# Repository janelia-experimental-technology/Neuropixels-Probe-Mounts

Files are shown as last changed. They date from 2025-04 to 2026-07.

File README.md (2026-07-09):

# Neuropixels-Probe-Mounts

Neuropixels probes are next-generation electrodes that record the activity of hundreds of neurons in the brain. They were developed through a collaboration funded by Howard Hughes Medical Institute, Wellcome Trust, Gatsby Charitable Foundation, and Allen Institute for Brain Science. The head of the collaboration is Tim Harris at HHMI Janelia Research Campus, and the electrodes are designed and fabricated by IMEC, the nanoelectronics research center. Further details may be found in the Harris lab, the University College London, and the Neuropixels home. 

Among the most annoying, time-consuming, and risky tasks when using these and similar Si probes is mounting the probe to a stereotaxic rod or a head post attached to a stereotaxic rod.  The dimensional accuracy of Neuropixels offers the opportunity to use the base as a mounting reference. To facilitate this, the latest versions of Neuropixels now ship with integrated dovetail mounting fixtures.  The fixture orients to the “metal cap,” actually a dovetail mounting adapter.

The technologies offered here are the accessories for mounting these probes and the mounting rod to dovetail adapter for several versions of these probes. These accessories were designed at HHMI's Janelia Research Campus by the Janelia Experimental Technologies group in collaboration with IMEC and end users. The first generation of Neuropixels, 1.0, had a prototype (3A) and production (3B) version. Designs for these versions include the probe holder or mounting rod, the dovetail mount, and the dovetail extension.  We also make available the accessories and assembly for Neuropixels 2.0, including the probe holder/mounting rod, dovetail mount, rod adapter, and assembly instructions. PDF and CAD files are included for convenience.

Opportunity: Free to make for Non-Profit Research by downloading the design here. See included hardware license.
Rights and designs available for Commercial License. Janelia makes no endorsements or guarantees of licensee products.

Neuropixel probes are available from IMEC: Neuropixels.org

Advantages: These accessories allow use of probes that did not originally ship with integrated dovetail mounting features. 

Construction: See the individual part drawings for more detail on fabricating each part. See the attached assembly models for the purchased commercial items needed to complete each probe assembly.

For inquiries, please contact innovation@janelia.hhmi.org and reference this repository.

To cite the designs, please use DOI: https://doi.org/10.25378/janelia.28810037

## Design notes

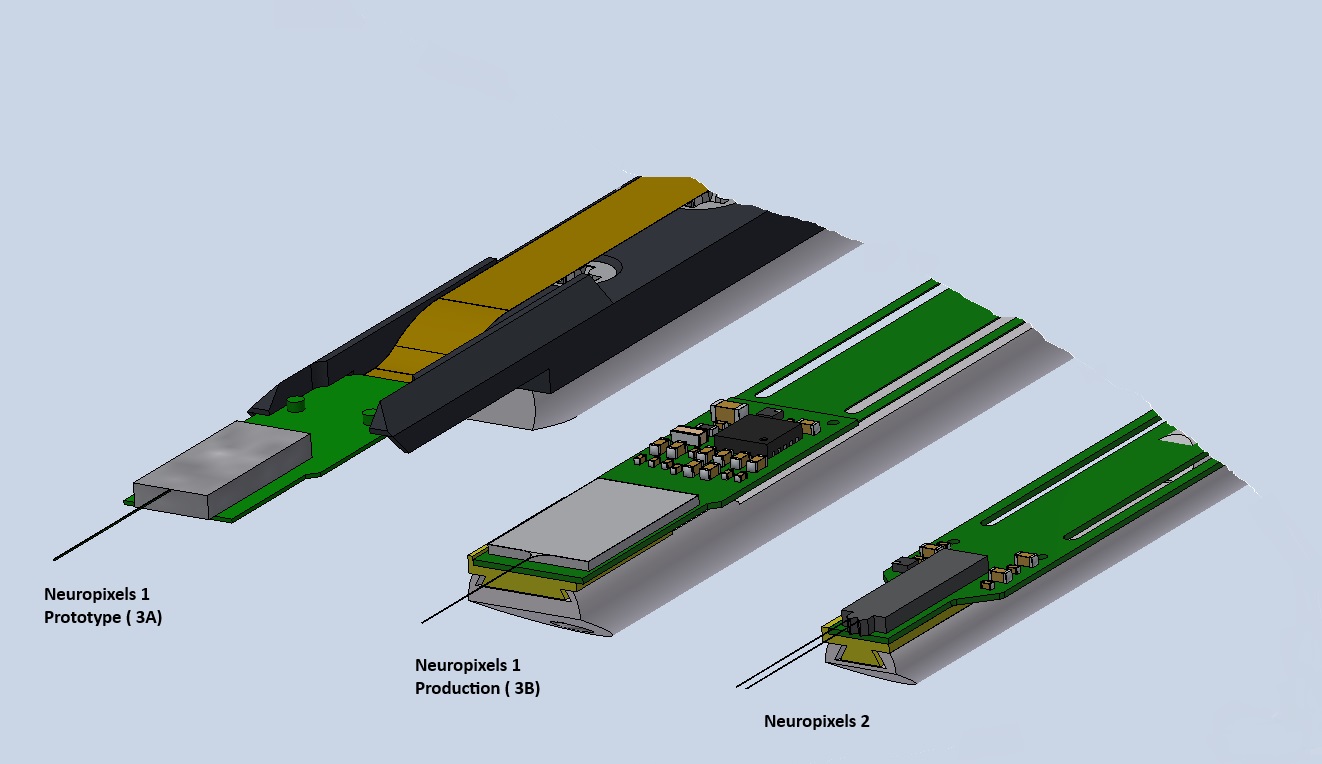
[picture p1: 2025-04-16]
Neuropixels Probe Comparison.jpg

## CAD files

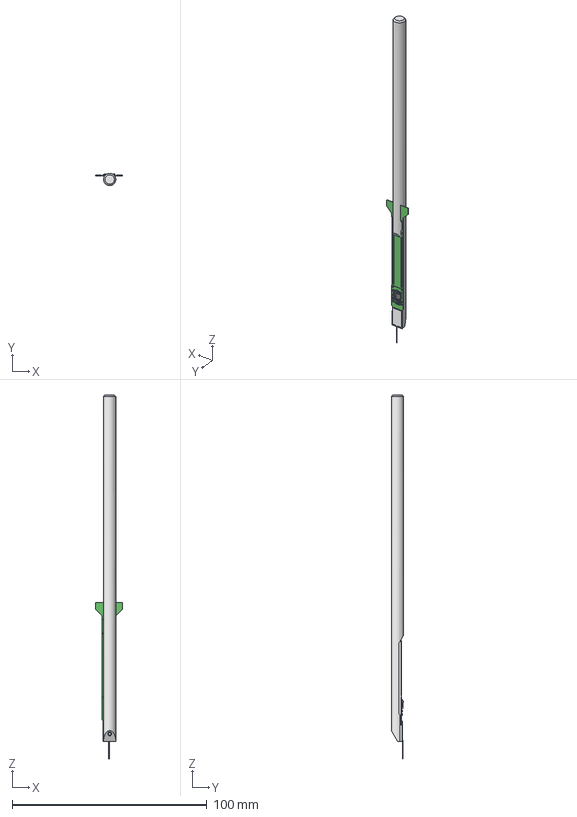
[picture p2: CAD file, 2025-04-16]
Neuropixels-1-Production-Mounts-3B/ASSEMBLY DRAWING AND MODEL/NEUROPIXELS GEN 1 PROBE ASSY 3B.stp
13.8 x 6.35 x 186.9 mm
J007778
J007869
NP2_FLEX_00-01
MISUMI SSHHI-SUS-M2.5-2.5

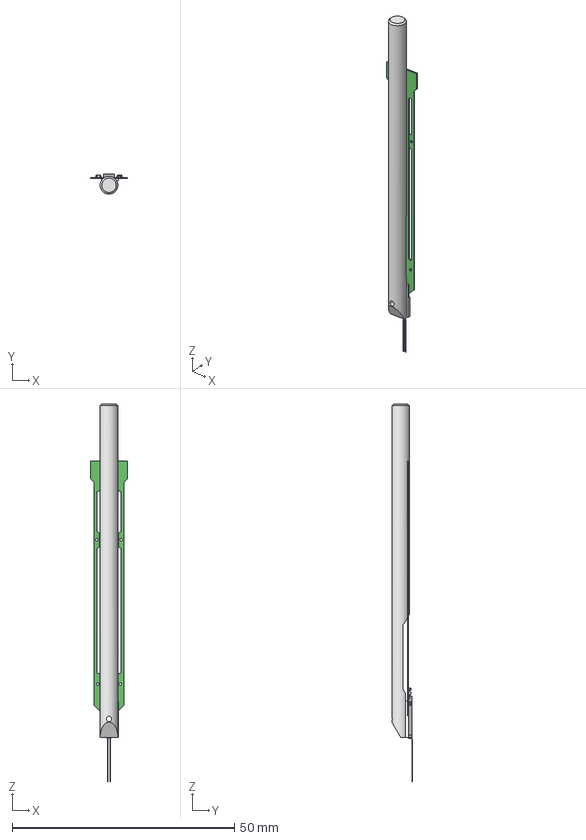
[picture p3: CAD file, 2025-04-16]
Neuropixels-2-Production-Mounts/ASSEMBLY DRAWING AND MODEL/NEUROPIXELS GEN 2 PROBE ASSY.stp
8.40 x 4.57 x 85.0 mm
J008040
J008039
NPM_FLEX_00-00

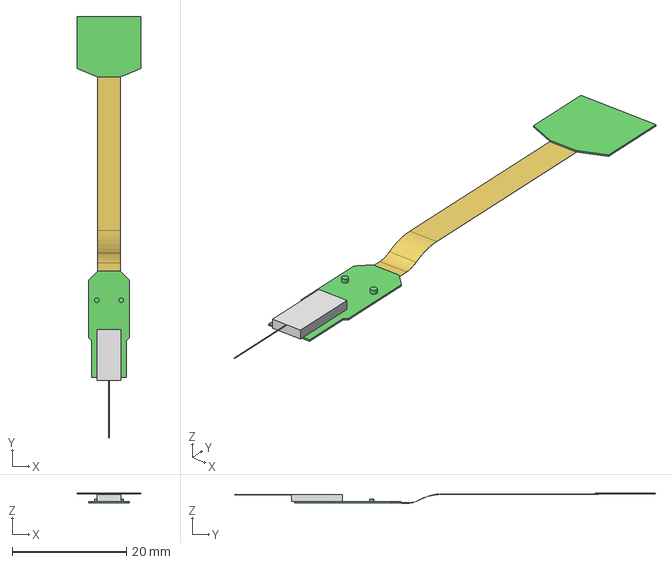
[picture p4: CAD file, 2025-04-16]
Neuropixels-1-Prototype-Mounts-3A/PART DRAWINGS AND MODELS/Neuropixels 1-3A Probe.stp
11.2 x 73.6 x 1.75 mm

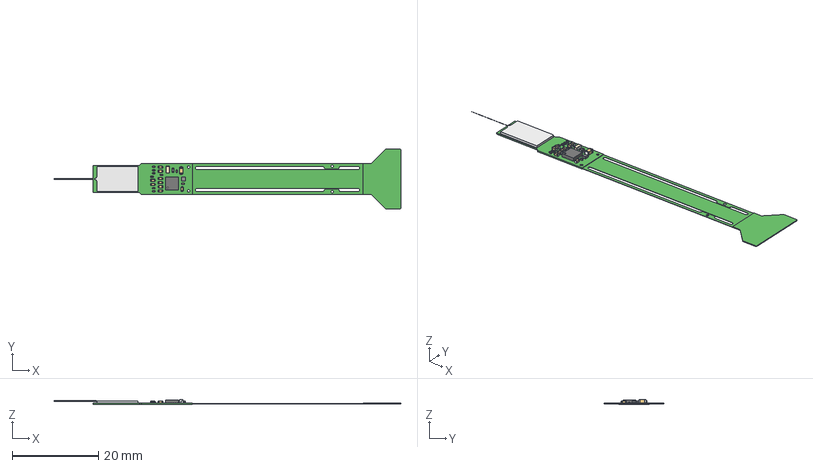
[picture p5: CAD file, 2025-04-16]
Neuropixels-1-Production-Mounts-3B/PART DRAWINGS AND MODELS/Neuropixels 1-3B Probe NP2_FLEX_00-01.stp
80.4 x 13.8 x 1.10 mm

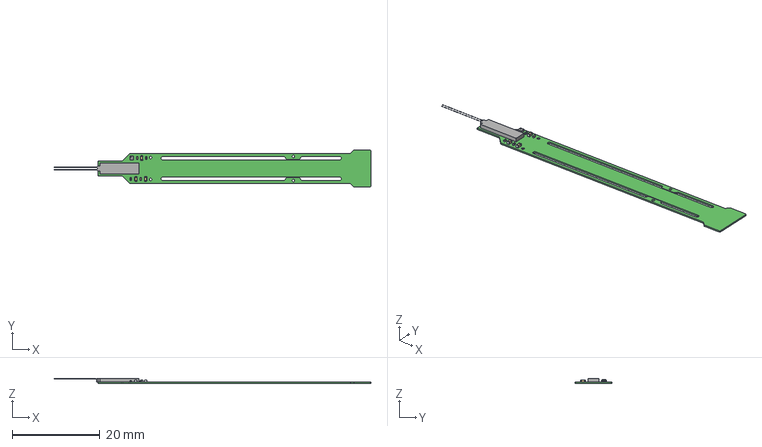
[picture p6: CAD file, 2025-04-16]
Neuropixels-2-Production-Mounts/PART DRAWINGS AND MODELS/Neuropixels 2-Probe NPM_FLEX_00-00.stp
72.2 x 8.40 x 1.10 mm

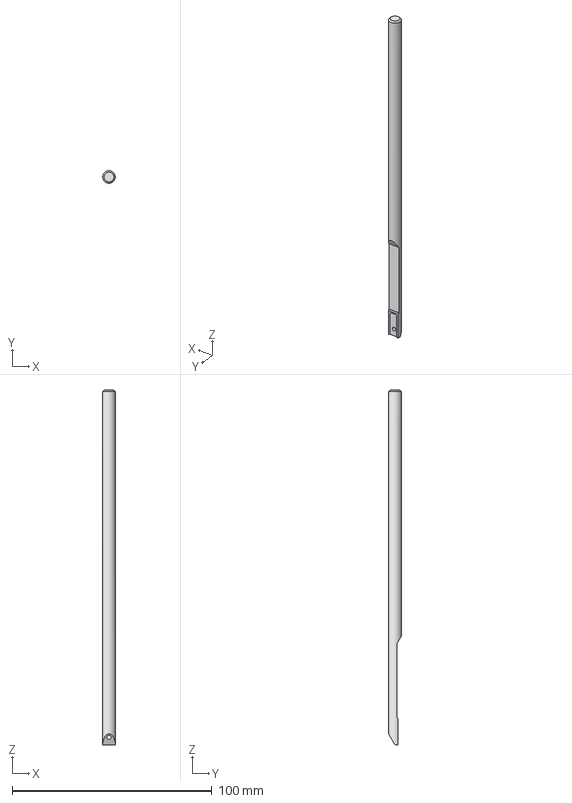
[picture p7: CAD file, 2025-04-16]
Neuropixels-1-Production-Mounts-3B/PART DRAWINGS AND MODELS/J007778 NEUROPIXELS DOVE TAIL PROBE HOLDER Rev A.STP
6.35 x 6.35 x 177.8 mm

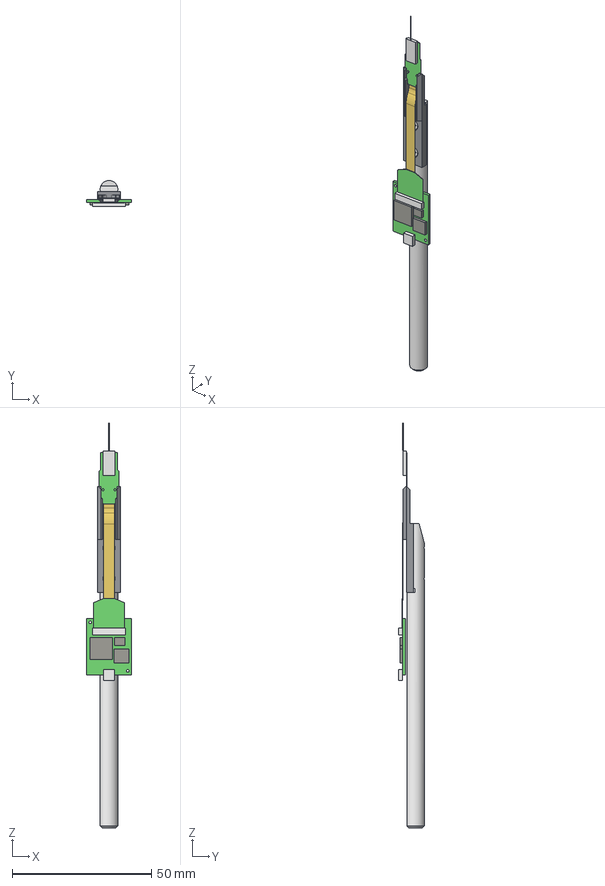
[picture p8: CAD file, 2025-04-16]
Neuropixels-1-Prototype-Mounts-3A/ASSEMBLY DRAWING AND MODEL/J007802 NEUROPIXEL 3A PROBE AND ROD HOLDER Rev -.stp
16.0 x 9.32 x 145.3 mm
NEUROPIXEL HEADSTAGE PCB
J007803
J007626
92010A003 x 2

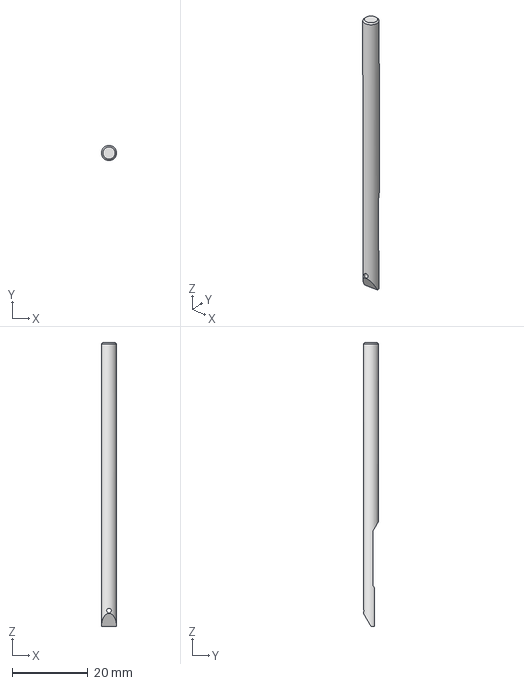
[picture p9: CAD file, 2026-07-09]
Neuropixels-2-Production-Mounts/PART DRAWINGS AND MODELS/J009776 NEUROPIXELS GEN 2 DOVE TAIL PROBE HOLDER_NARROW Rev B.stp
4.00 x 4.00 x 75.0 mm

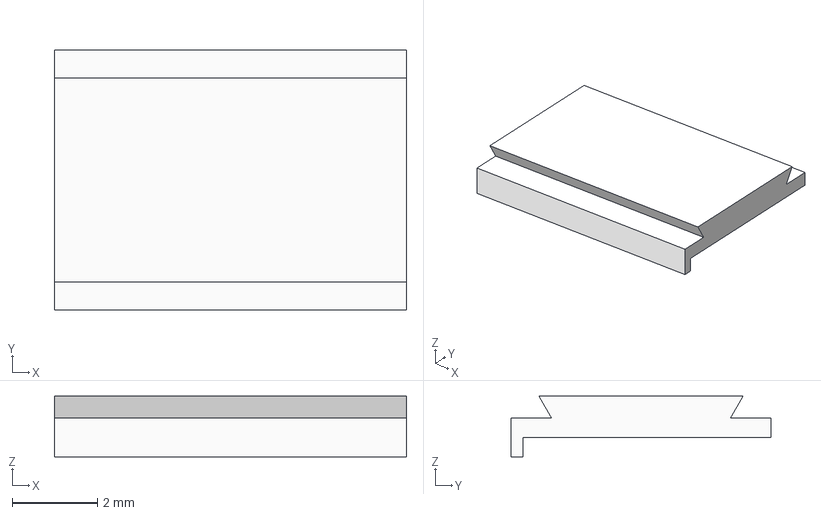
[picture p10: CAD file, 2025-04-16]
Neuropixels-1-Production-Mounts-3B/PART DRAWINGS AND MODELS/J007869 NEUROPIXELS DOVE TAIL MOUNT Rev -.stp
8.25 x 6.10 x 1.42 mm

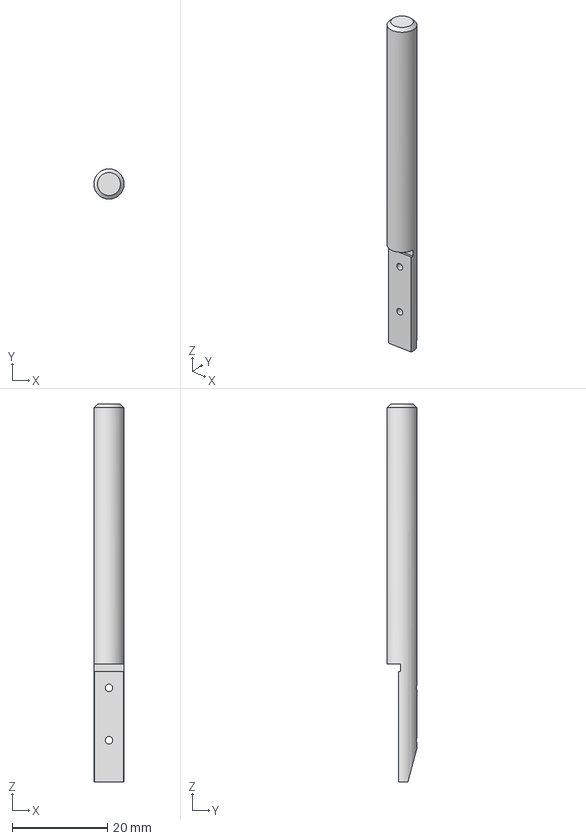
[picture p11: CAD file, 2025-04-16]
Neuropixels-1-Prototype-Mounts-3A/PART DRAWINGS AND MODELS/J007474 PTR PROBE MOUNT ROD Rev -.stp
6.35 x 6.35 x 79.4 mm

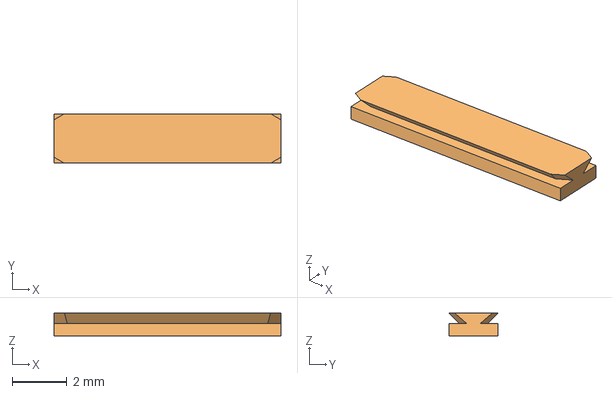
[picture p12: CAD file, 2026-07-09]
Neuropixels-2-Production-Mounts/PART DRAWINGS AND MODELS/J009777 NEUROPIXELS DOVE TAIL MOUNT GEN 2_NARROW Rev C.stp
8.25 x 1.80 x 0.825 mm

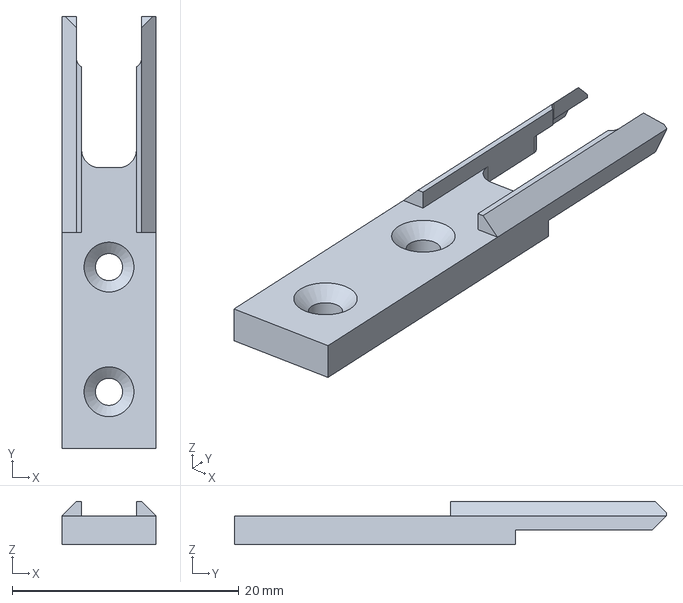
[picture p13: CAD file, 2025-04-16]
Neuropixels-1-Prototype-Mounts-3A/PART DRAWINGS AND MODELS/J007803 NEUROPIXEL 3A PROBE BASE Rev -.stp
8.25 x 38.1 x 3.81 mm

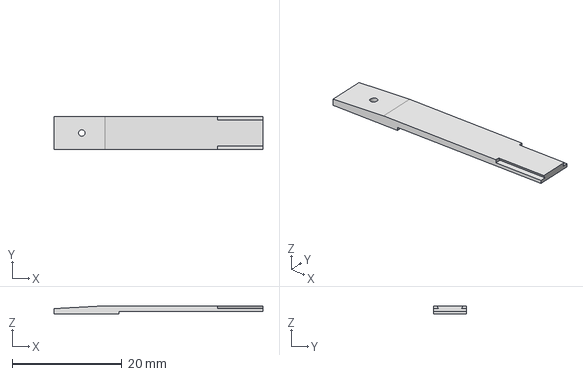
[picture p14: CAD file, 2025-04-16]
Neuropixels-1-Production-Mounts-3B/PART DRAWINGS AND MODELS/J007777 IMEC DOVE TAIL EXTENSION Rev -.stp
38.1 x 6.10 x 1.52 mm

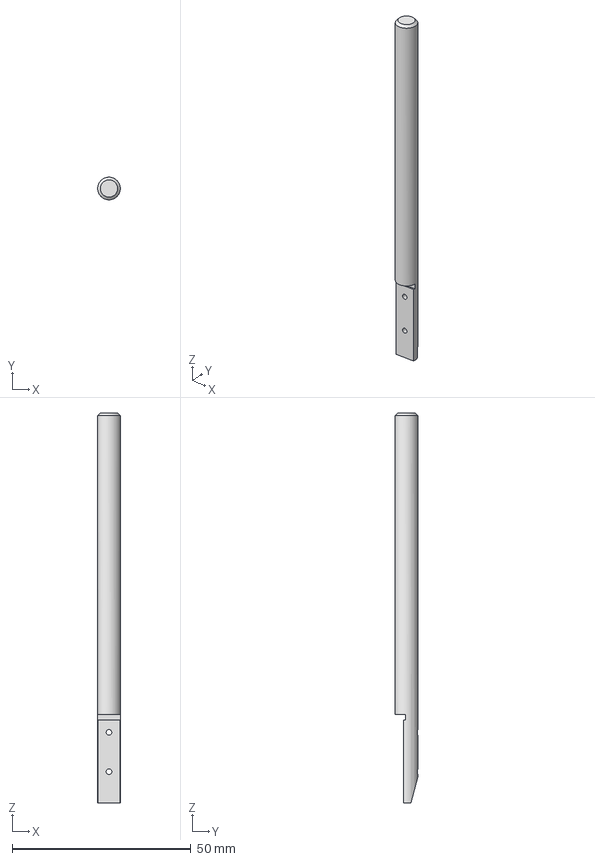
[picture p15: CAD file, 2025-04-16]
Neuropixels-1-Prototype-Mounts-3A/PART DRAWINGS AND MODELS/J007626 PTR PROBE MOUNT ROD EXTENDED Rev -.stp
6.35 x 6.35 x 109.2 mm

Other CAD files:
Neuropixels-2-Production-Mounts/PART DRAWINGS AND MODELS/J008039 NEUROPIXELS DOVE TAIL MOUNT GEN 2 Rev -.stp
Neuropixels-2-Production-Mounts/PART DRAWINGS AND MODELS/J008040 NEUROPIXELS GEN 2 DOVE TAIL PROBE HOLDER Rev -.stp
Neuropixels-2-Production-Mounts/PART DRAWINGS AND MODELS/J008574 NEUROPIXELS GEN 2 ROD ADAPTER Rev -.stp
Neuropixels-1-Production-Mounts-3B/INVENTOR PACK AND GO/MISUMI SSHHI-SUS-M2.5-2.5.ipt
Neuropixels-1-Production-Mounts-3B/INVENTOR PACK AND GO/NEUROPIXELS DOVE TAIL MOUNT.ipt
Neuropixels-1-Production-Mounts-3B/INVENTOR PACK AND GO/NEUROPIXELS DOVE TAIL PROBE HOLDER.ipt
Neuropixels-1-Production-Mounts-3B/INVENTOR PACK AND GO/NEUROPIXELS GEN 1 PROBE ASSY.iam
Neuropixels-1-Production-Mounts-3B/INVENTOR PACK AND GO/NP2_FLEX_00-01.ipt
Neuropixels-1-Production-Mounts-3B/PART DRAWINGS AND MODELS/J007777 IMEC DOVE TAIL EXTENSION Rev -.ipt
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

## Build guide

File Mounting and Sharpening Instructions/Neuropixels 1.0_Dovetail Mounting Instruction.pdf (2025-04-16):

## Dovetail Accessory Mounting W.Sun 1/28/2019

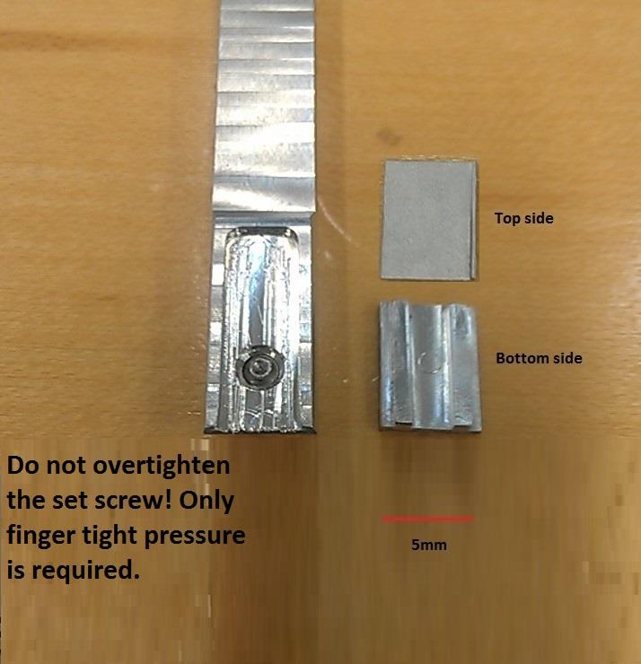
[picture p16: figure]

Top and bottom surface of the part to be attached to the “back side” of the 3B probe, opposite of components.

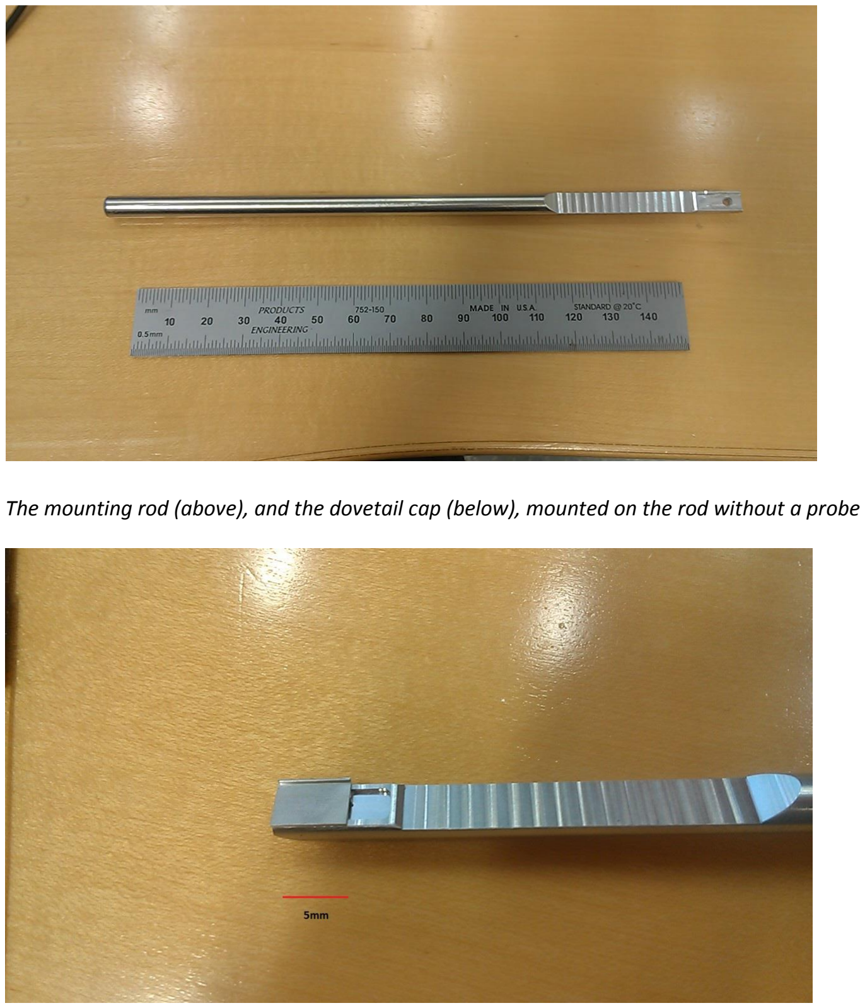
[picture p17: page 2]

The mounting rod (above), and the dovetail cap (below), mounted on the rod without a probe

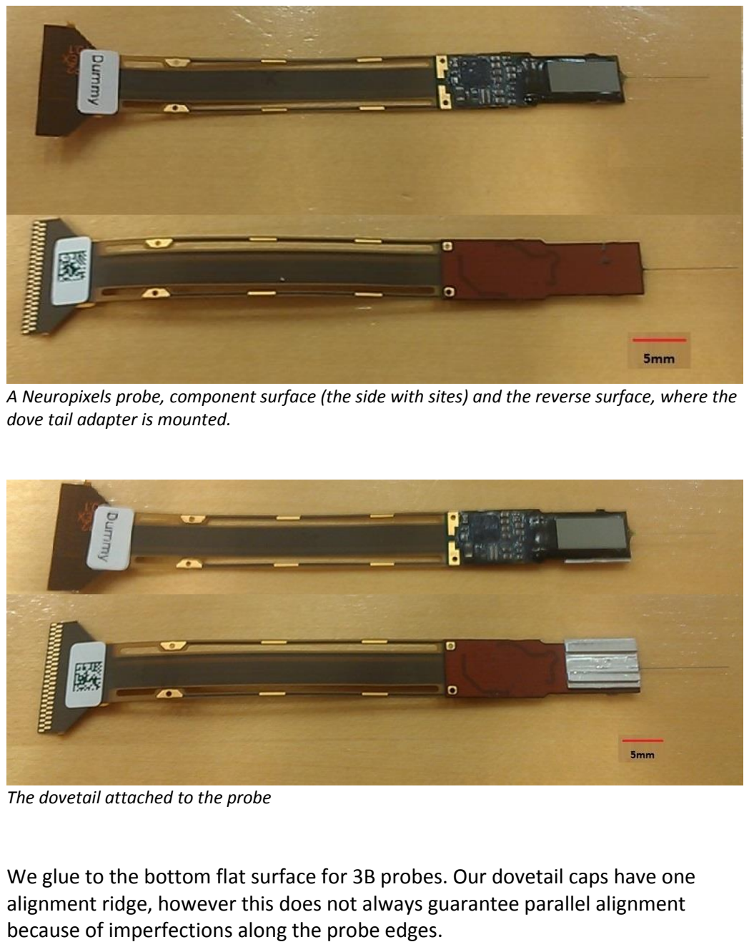
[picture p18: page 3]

A Neuropixels probe, component surface (the side with sites) and the reverse surface, where the dove tail adapter is mounted.

The dovetail attached to the probe

We glue to the bottom flat surface for 3B probes. Our dovetail caps have one alignment ridge, however this does not always guarantee parallel alignment because of imperfections along the probe edges.

Therefore, we use a Mitutoyo Profile Projector Machine PH-3500.

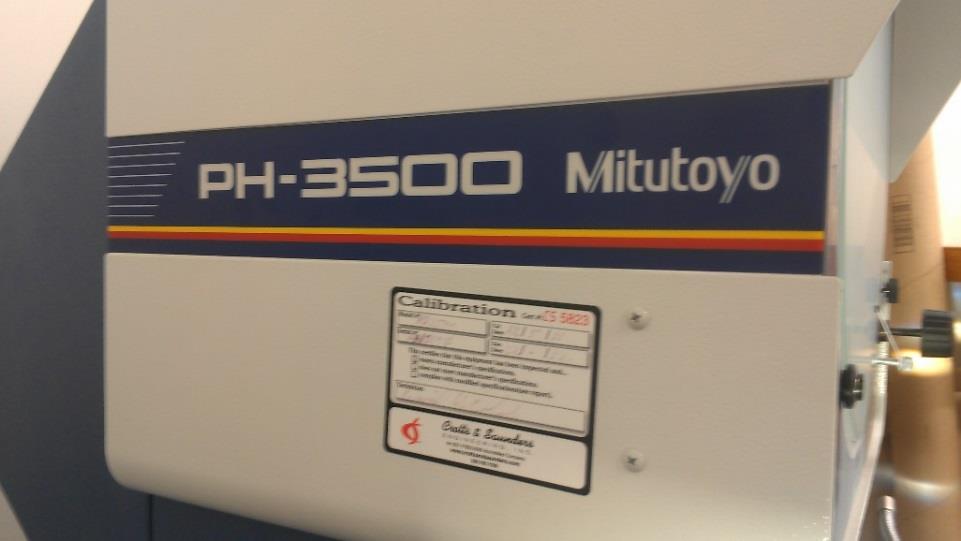
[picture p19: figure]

Dovetail pieces are aligned parallel with the electrode shank, and glued with cyanoacrylate gel type Krazy Glue (Part KG866).

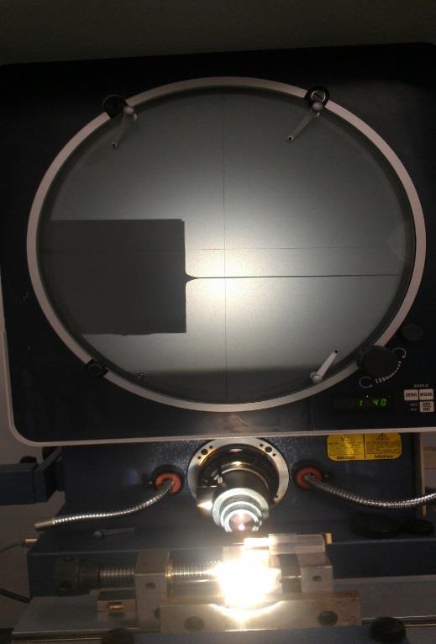
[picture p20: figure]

For best adhesion, a sandblaster is used to roughen the surface of the caps, and both surfaces are cleaned with IPA before gluing. The probe is temporarily affixed to a movable fixture, then placed onto the profile machine. The dovetail cap is fixed to the rod to permit handling and positioning during the gluing process. Total thickness: 2.1mm

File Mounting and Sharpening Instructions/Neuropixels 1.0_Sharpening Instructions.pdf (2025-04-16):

Electrode sharpening | W.Sun 1/28/2019

Using an opened HDD Hard Drive, a 0.3um aluminum oxide polishing pad (PF00.3A-P-4) is adhered to the top surface of the HDD platter. Due to the nature of this procedure, protective eyewear is recommended.

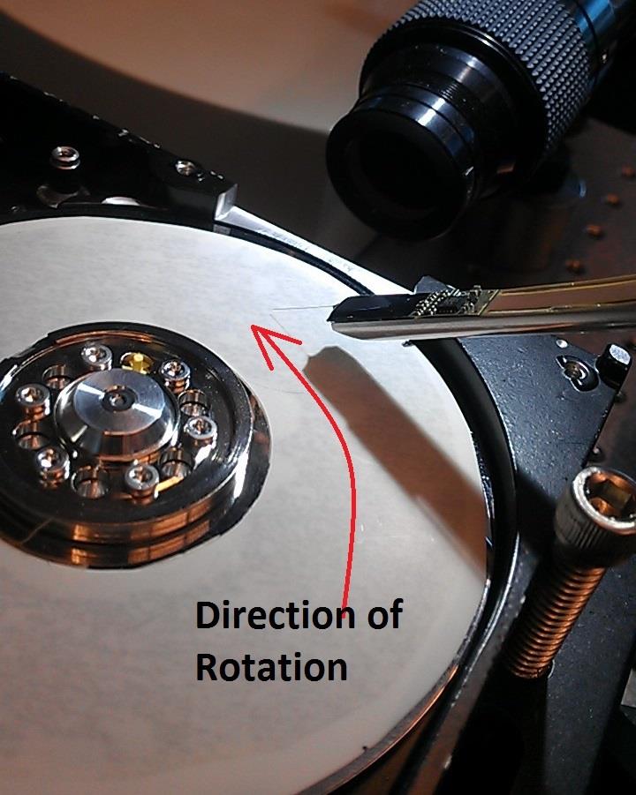
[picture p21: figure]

Our setup utilizes a dovetail probe holder, which can be lowered and tilted. Orient the probe with the sites facing up, and the bottom surface to be chiseled by the rotating polisher. The sharpening angle used is approximately 38 degrees. As seen in the picture above, from top (overhead) view, position the shank along a tangent of the spinning platter, with the tip pointing in the direction of rotation (in our case, the HDD spins CCW).

Upon the point of contacting the tip to the polisher, the probe should not be lowered further. Polishing time varies with RPMs, polishing location on the spinning HDD (OD is faster than ID), polishing pad grit, and other factors. It is best to polish conservatively and re-examine the tip as you proceed to gain some insight about the polishing time for your particular setup. In our case, it takes around 25 seconds.

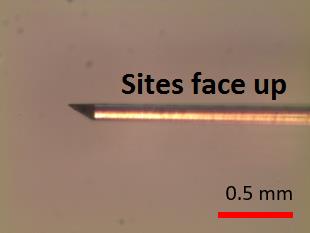
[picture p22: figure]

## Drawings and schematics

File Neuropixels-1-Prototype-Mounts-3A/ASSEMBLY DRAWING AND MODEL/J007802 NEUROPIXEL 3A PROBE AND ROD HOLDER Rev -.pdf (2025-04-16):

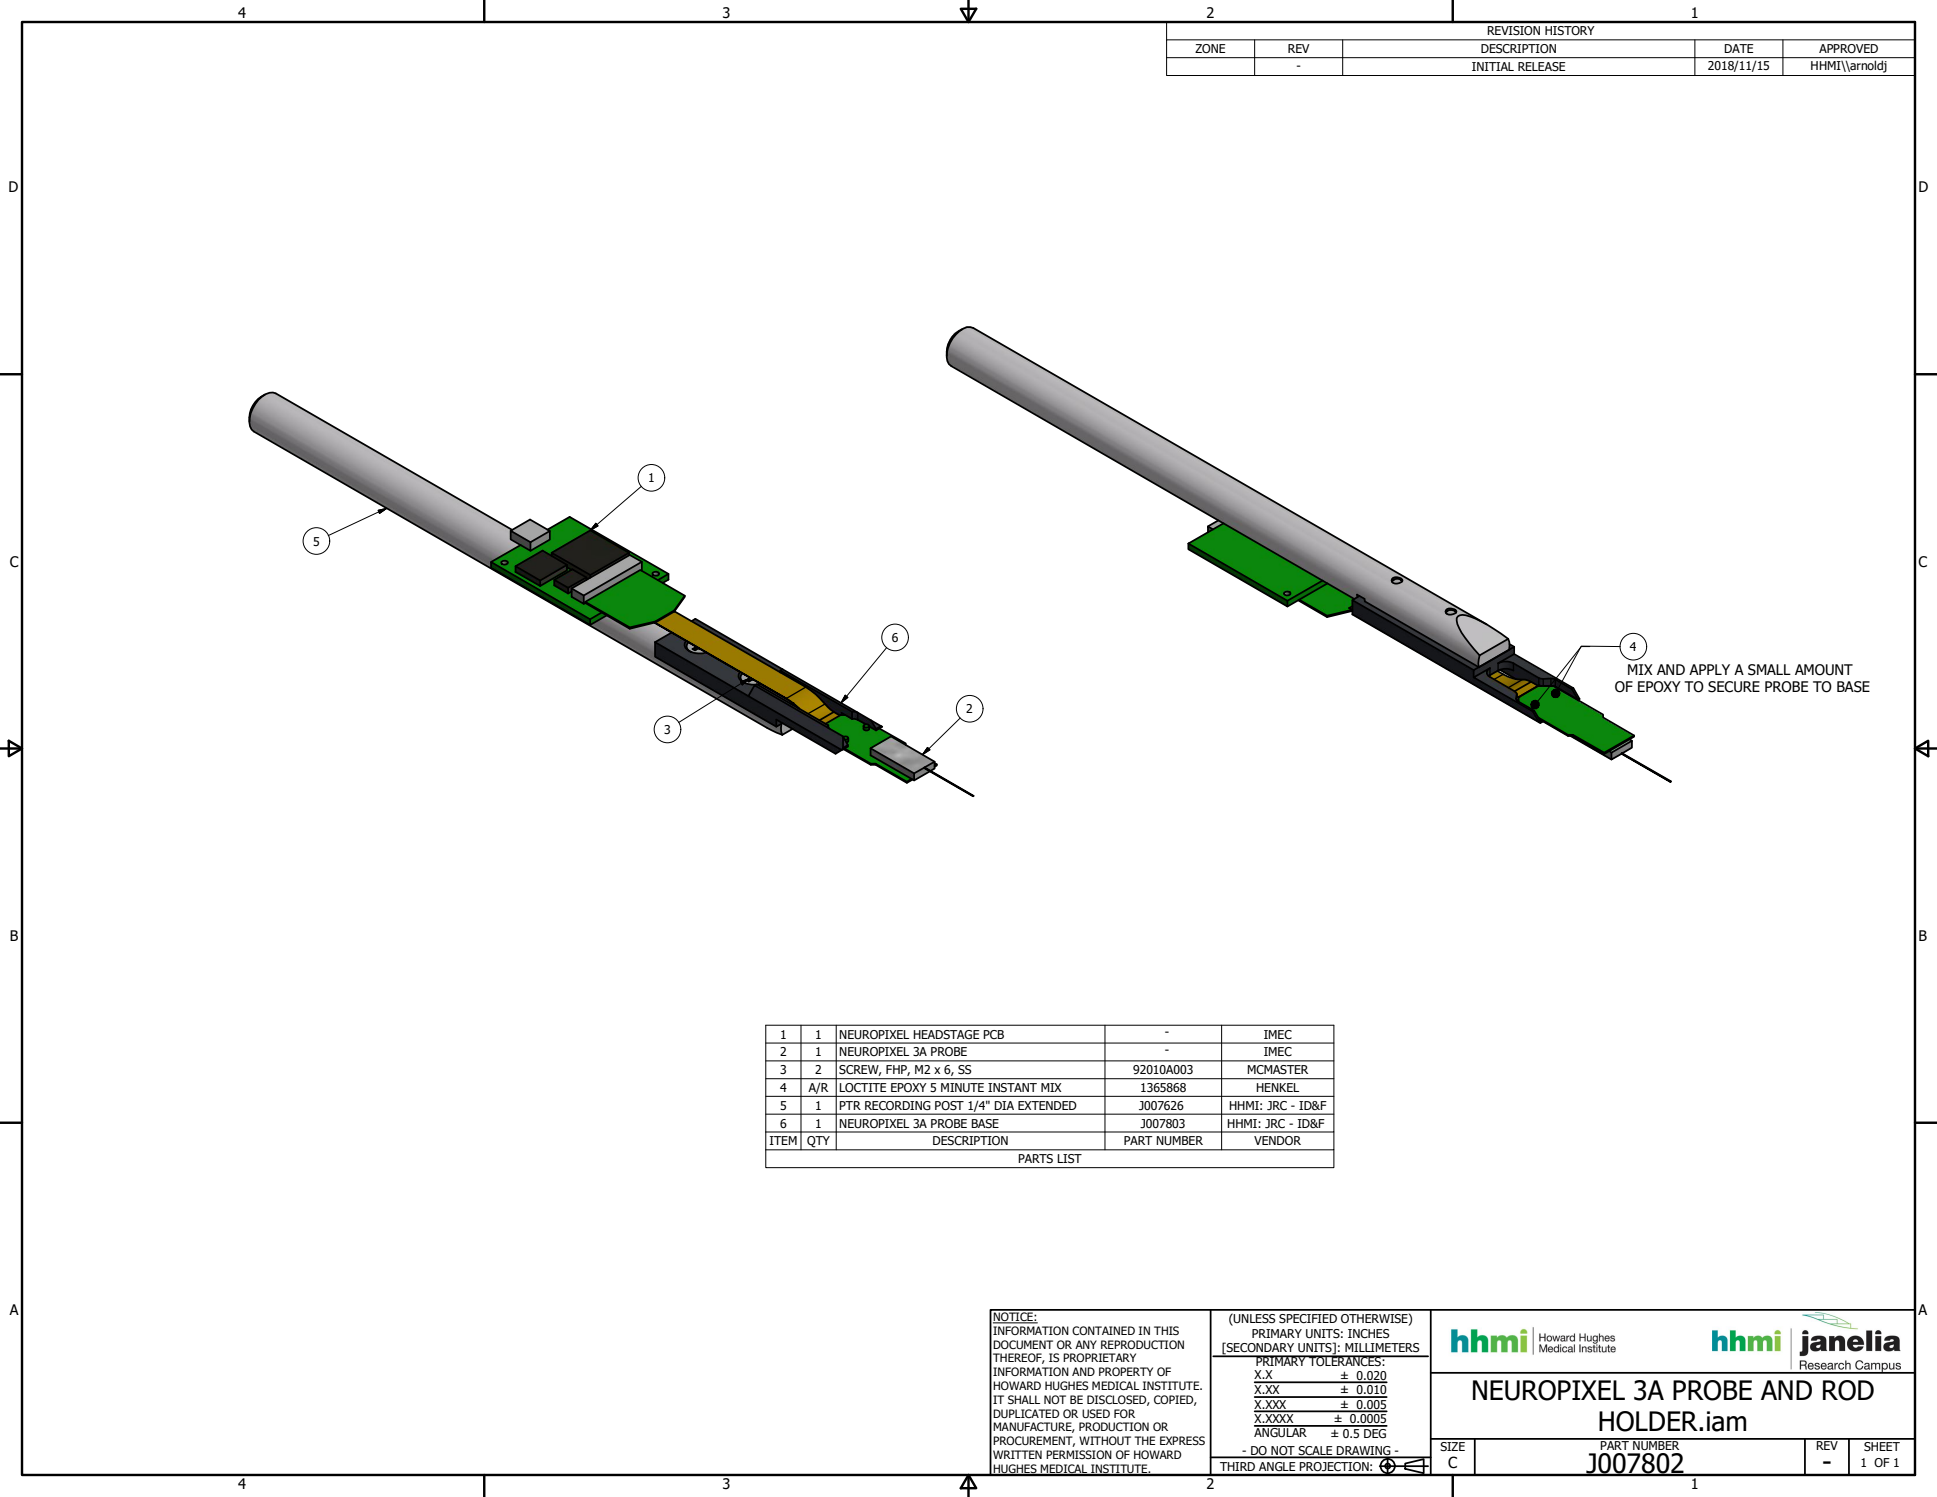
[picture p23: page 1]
PARTS LIST; PART NUMBER; 1 OF 1 THIRD ANGLE PROJECTION:; ± 0.020 ± 0.010 ± 0.005 ± 0.0005 ± 0.5 DEG; REVISION HISTORY

ZONE | REV | DESCRIPTION | DATE | APPROVED

- | INITIAL RELEASE | 2018/11/15 | HHMI\\arnoldj

MIX AND APPLY A SMALL AMOUNT
OF EPOXY TO SECURE PROBE TO BASE

1 | 1 | NEUROPIXEL HEADSTAGE PCB | - | IMEC
2 | 1 | NEUROPIXEL 3A PROBE | - | IMEC
3 | 2 | SCREW, FHP, M2 x 6, SS | 92010A003 | MCMASTER
4 | A/R | LOCTITE EPOXY 5 MINUTE INSTANT MIX | 1365868 | HENKEL
5 | 1 | PTR RECORDING POST 1/4" DIA EXTENDED | J007626 | HHMI: JRC - ID&F
6 | 1 | NEUROPIXEL 3A PROBE BASE | J007803 | HHMI: JRC - ID&F
ITEM | QTY | DESCRIPTION | PART NUMBER | VENDOR

NOTICE:
INFORMATION CONTAINED IN THIS
DOCUMENT OR ANY REPRODUCTION
THEREOF, IS PROPRIETARY
INFORMATION AND PROPERTY OF
HOWARD HUGHES MEDICAL INSTITUTE.
IT SHALL NOT BE DISCLOSED, COPIED,
DUPLICATED OR USED FOR
MANUFACTURE, PRODUCTION OR
PROCUREMENT, WITHOUT THE EXPRESS
WRITTEN PERMISSION OF HOWARD
HUGHES MEDICAL INSTITUTE.

(UNLESS SPECIFIED OTHERWISE)
PRIMARY UNITS: INCHES
[SECONDARY UNITS]: MILLIMETERS
PRIMARY TOLERANCES:
X.XXX
X.XXXX
ANGULAR
- DO NOT SCALE DRAWING -

NEUROPIXEL 3A PROBE AND ROD

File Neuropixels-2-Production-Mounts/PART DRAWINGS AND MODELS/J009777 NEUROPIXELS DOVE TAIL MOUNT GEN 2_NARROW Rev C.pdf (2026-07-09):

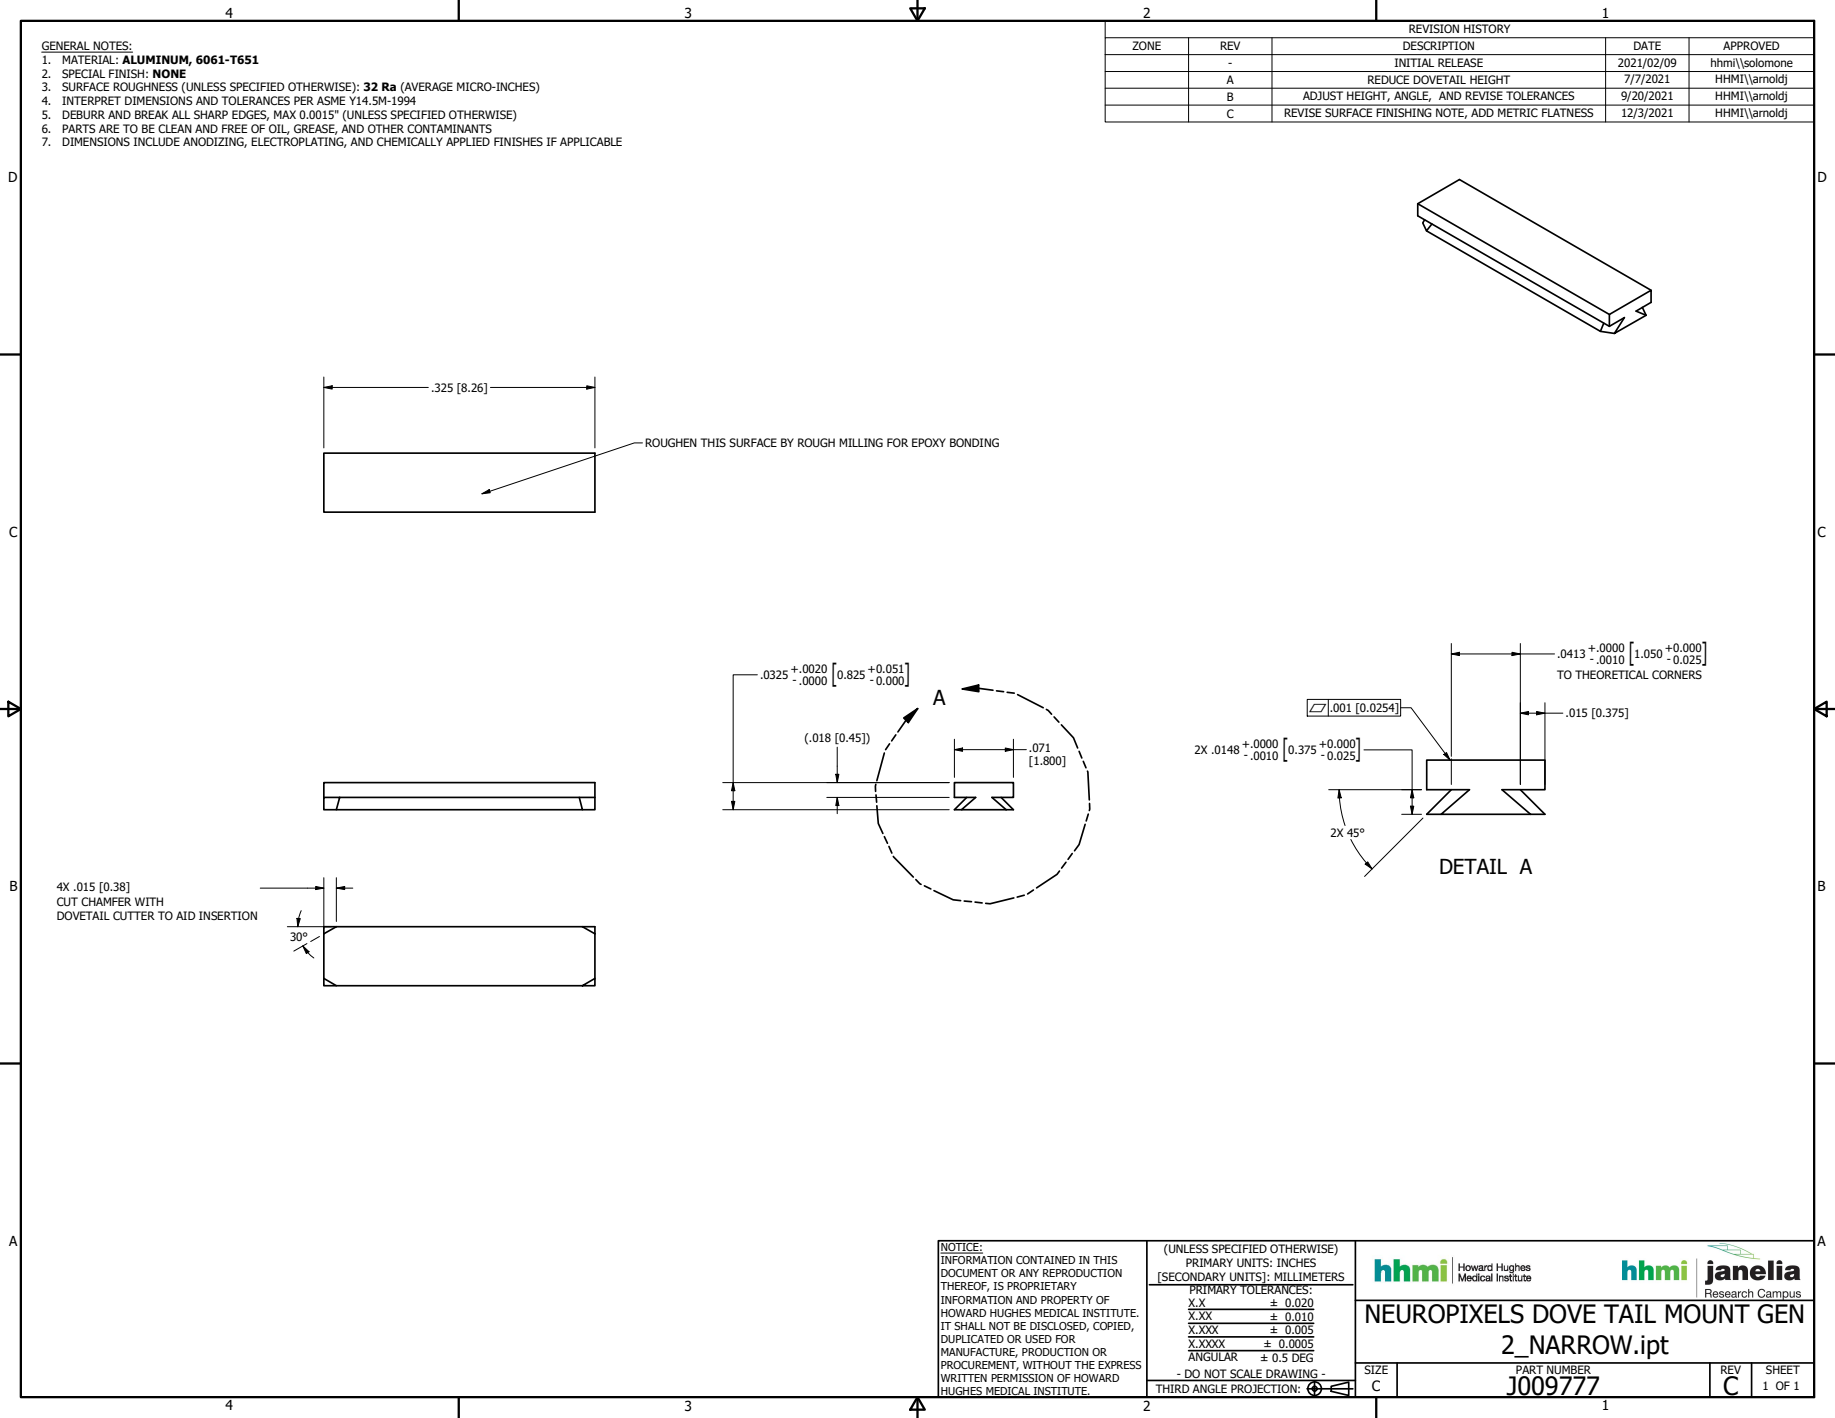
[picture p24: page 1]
DETAIL A; PART NUMBER; 1 OF 1 THIRD ANGLE PROJECTION:; ± 0.020 ± 0.010 ± 0.005 ± 0.0005 ± 0.5 DEG; REVISION HISTORY; - 0.025 TO THEORETICAL CORNERS

GENERAL NOTES:
1. MATERIAL: ALUMINUM, 6061-T651
2. SPECIAL FINISH: NONE
3. SURFACE ROUGHNESS (UNLESS SPECIFIED OTHERWISE): 32 Ra (AVERAGE MICRO-INCHES)
4. INTERPRET DIMENSIONS AND TOLERANCES PER ASME Y14.5M-1994
5. DEBURR AND BREAK ALL SHARP EDGES, MAX 0.0015" (UNLESS SPECIFIED OTHERWISE)
6. PARTS ARE TO BE CLEAN AND FREE OF OIL, GREASE, AND OTHER CONTAMINANTS
7. DIMENSIONS INCLUDE ANODIZING, ELECTROPLATING, AND CHEMICALLY APPLIED FINISHES IF APPLICABLE

ZONE | REV | DESCRIPTION | DATE | APPROVED

- | INITIAL RELEASE | 2021/02/09 | hhmi\\solomone
A | REDUCE DOVETAIL HEIGHT | 7/7/2021 | HHMI\\arnoldj
B | ADJUST HEIGHT, ANGLE, AND REVISE TOLERANCES | 9/20/2021 | HHMI\\arnoldj
C | REVISE SURFACE FINISHING NOTE, ADD METRIC FLATNESS | 12/3/2021 | HHMI\\arnoldj

ROUGHEN THIS SURFACE BY ROUGH MILLING FOR EPOXY BONDING

CUT CHAMFER WITH
DOVETAIL CUTTER TO AID INSERTION

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

NEUROPIXELS DOVE TAIL MOUNT GEN

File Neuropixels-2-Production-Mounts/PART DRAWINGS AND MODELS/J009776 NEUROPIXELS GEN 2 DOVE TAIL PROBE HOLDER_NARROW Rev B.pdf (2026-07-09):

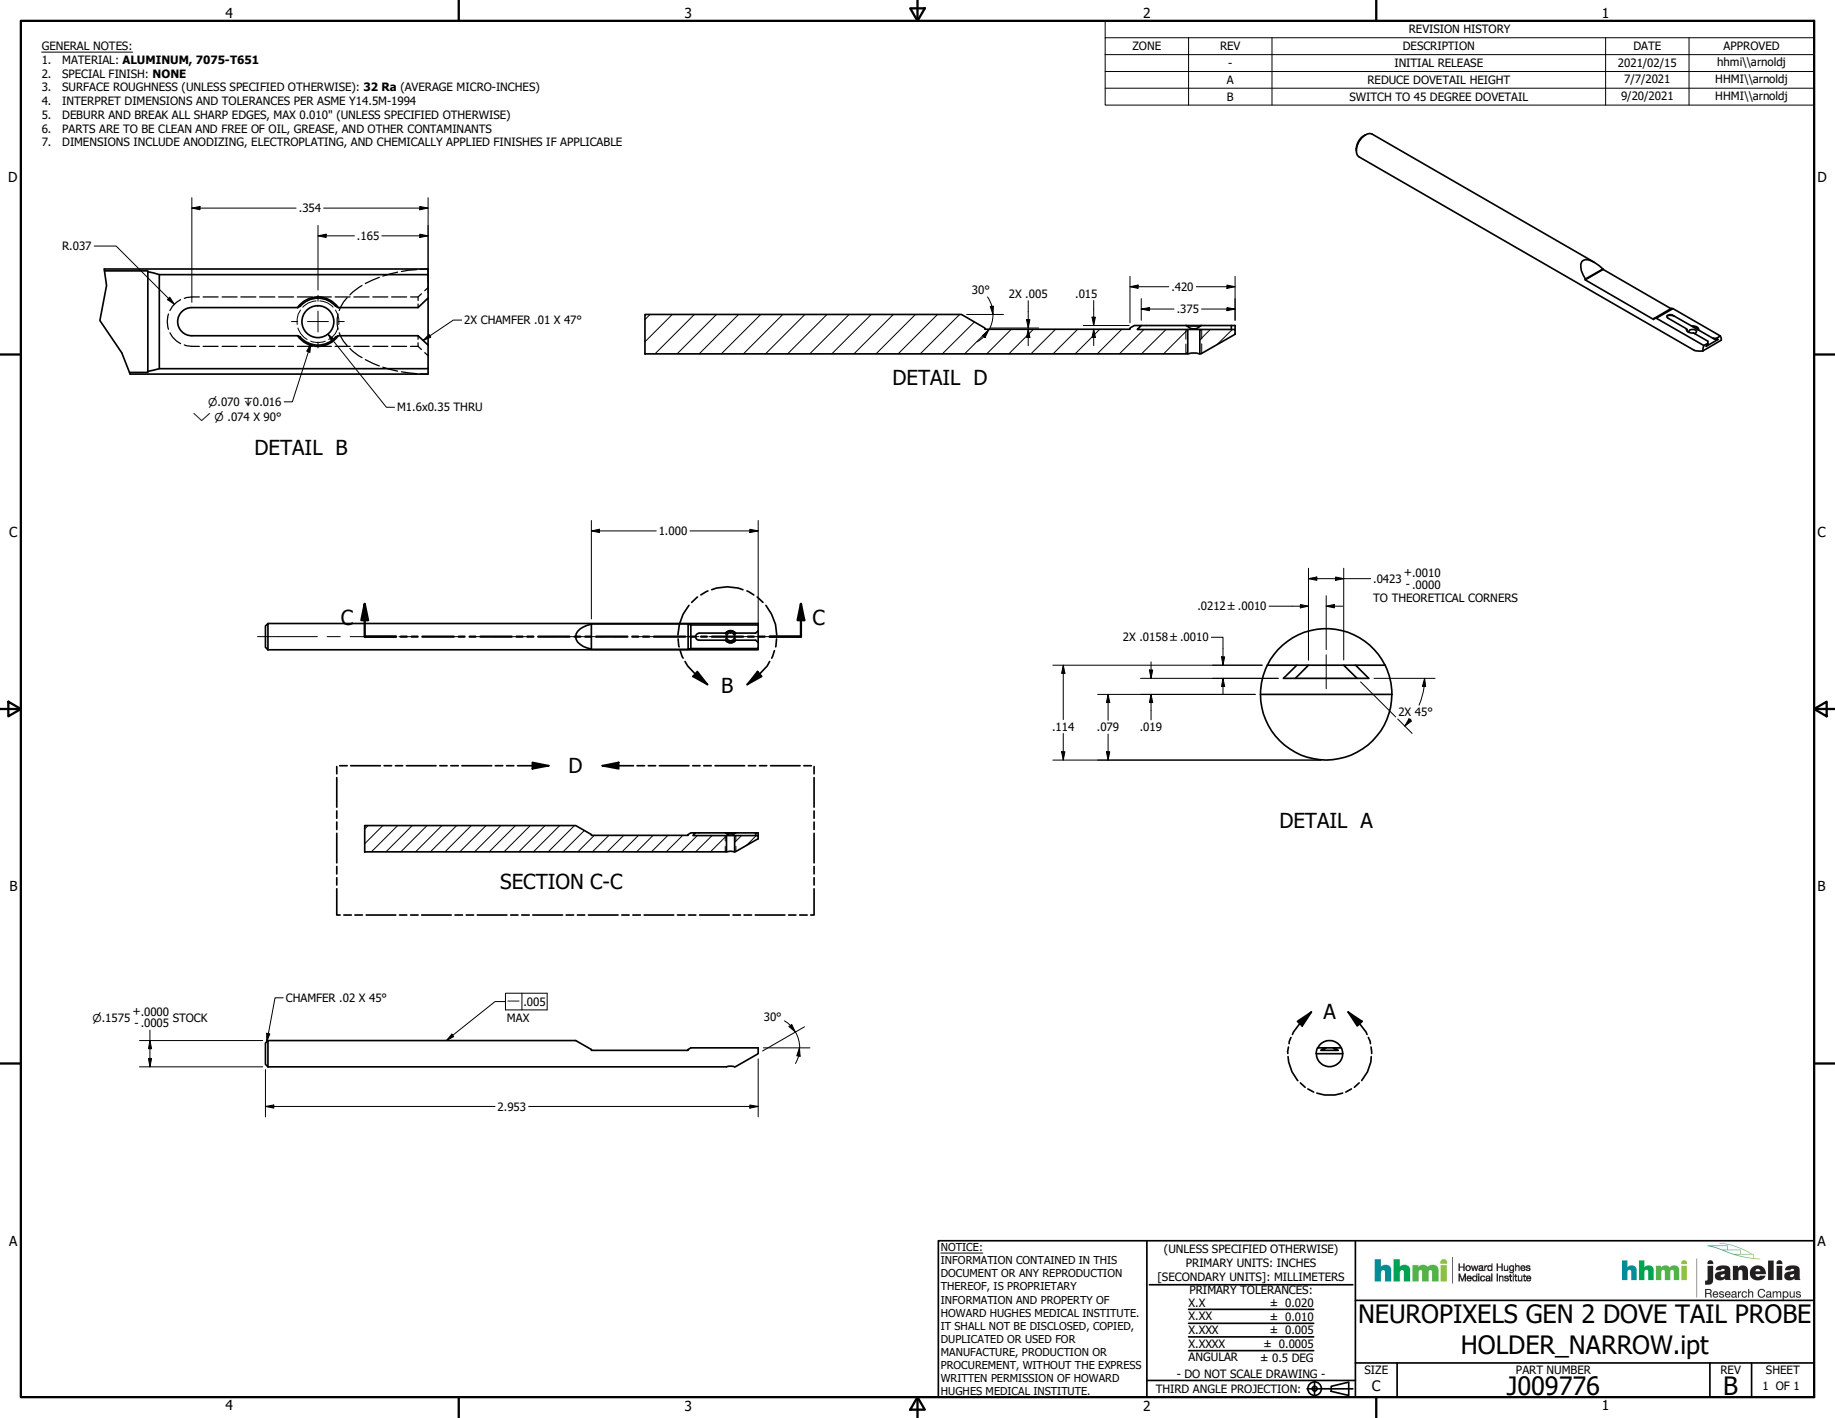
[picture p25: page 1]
DETAIL A; DETAIL B; SECTION C-C; DETAIL D; PART NUMBER; 1 OF 1 THIRD ANGLE PROJECTION:; ± 0.020 ± 0.010 ± 0.005 ± 0.0005 ± 0.5 DEG; REVISION HISTORY; CHAMFER .02 X 45°; 2X CHAMFER .01 X 47°; M1.6x0.35 THRU; - .0000 TO THEORETICAL CORNERS

GENERAL NOTES:
1. MATERIAL: ALUMINUM, 7075-T651
2. SPECIAL FINISH: NONE
3. SURFACE ROUGHNESS (UNLESS SPECIFIED OTHERWISE): 32 Ra (AVERAGE MICRO-INCHES)
4. INTERPRET DIMENSIONS AND TOLERANCES PER ASME Y14.5M-1994
5. DEBURR AND BREAK ALL SHARP EDGES, MAX 0.010" (UNLESS SPECIFIED OTHERWISE)
6. PARTS ARE TO BE CLEAN AND FREE OF OIL, GREASE, AND OTHER CONTAMINANTS
7. DIMENSIONS INCLUDE ANODIZING, ELECTROPLATING, AND CHEMICALLY APPLIED FINISHES IF APPLICABLE

ZONE | REV | DESCRIPTION | DATE | APPROVED

- | INITIAL RELEASE | 2021/02/15 | hhmi\\arnoldj
A | REDUCE DOVETAIL HEIGHT | 7/7/2021 | HHMI\\arnoldj
B | SWITCH TO 45 DEGREE DOVETAIL | 9/20/2021 | HHMI\\arnoldj

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

NEUROPIXELS GEN 2 DOVE TAIL PROBE
